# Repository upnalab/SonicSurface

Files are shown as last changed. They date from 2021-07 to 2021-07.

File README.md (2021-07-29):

# SonicSurface
An Open ultrasonic phased-array for applications in acoustic levitation, haptic feedback, directive audio and many more.

# Contents of this Repository
Algorithms - Algorithms to generate different patterns
Electronics - PCB gerber files and bill of materials
Firmware - Code to be upload in the FPGA boards that control the arrays
Mech - Mechanical parts for 3d printing or lasercutting

# How to Assemble and example Applications
- Instructables: https://www.instructables.com/SonicSurface-Phased-array-for-Levitation-Mid-air-T/
- Video: https://www.youtube.com/watch?v=vAEZvYlUnEM
- Paper: https://doi.org/10.3390/app11072981

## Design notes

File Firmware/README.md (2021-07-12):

FPGA jic are the code to upload into the FPGA using the Blaster device (or any other compatible one) they are the precompiled verions of what is in the project folder. They have no phase calibration for the emitters so you should do one of the following:
1) solder the transducers with the right polarity
2) put the phase calibration on the simulation
3) recompile the project into a new jic with the calibration hardcoded

FPGAPrimary is enabled with the command 192 and generates its own clock on port D
FPGASecondary is enabled with the command 192 and syncs its clock with what is input in port A
FPGATactileModulation is a Primary board that modulates the emitted waves at 200Hz (or at a config speed). 

ESP contain optional controllers. The haptic controller is designed to be used with FPGATactileModulation

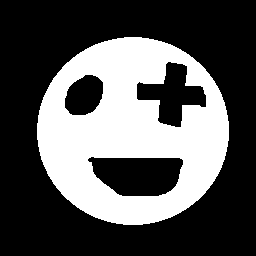
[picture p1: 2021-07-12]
Algorithms/EmissionPhasesAmpsForTargetSlice/smiley.png

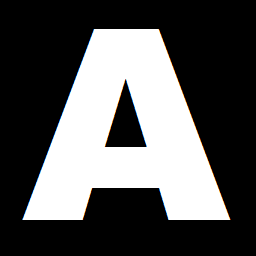
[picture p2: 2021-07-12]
Algorithms/EmissionPhasesAmpsForTargetSlice/target_a.png

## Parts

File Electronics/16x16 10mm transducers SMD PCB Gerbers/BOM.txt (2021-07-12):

the size of the PCB is 183 x 169mm 2 layers

128x MIC4127 SOIC8
32x 74hc595 SOIC16
160x 0.1uf capacitors 50v 0805
1x dc barrel
head connectors for the FPGA (2x22) and lateral connectors

256x transducers ideally the ones used for TinyLev (Check for Instructables Acoustic Levitator)

Other pin compatible drivers are: TC4427a or MIC4127  / MIC4478 for 32V but pricey as hell

The FPGA is this one: https://www.waveshare.com/coreep4ce6.htm

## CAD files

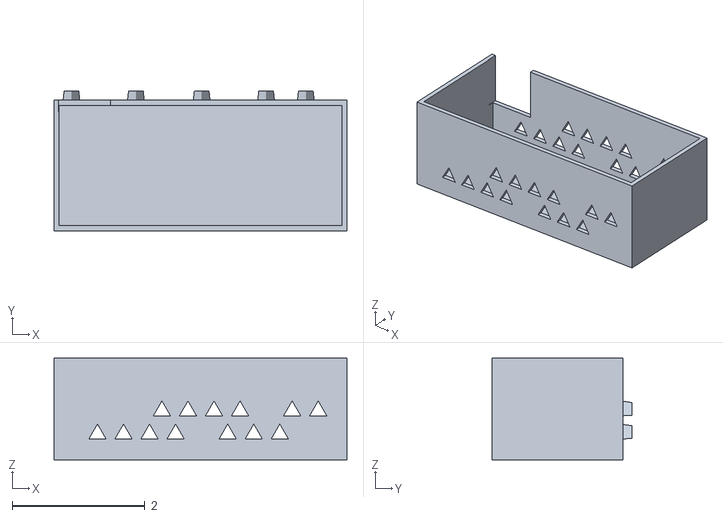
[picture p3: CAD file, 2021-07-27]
Mech/board case/SonicSurfaceHolder.stl
4.41 x 2.10 x 1.53

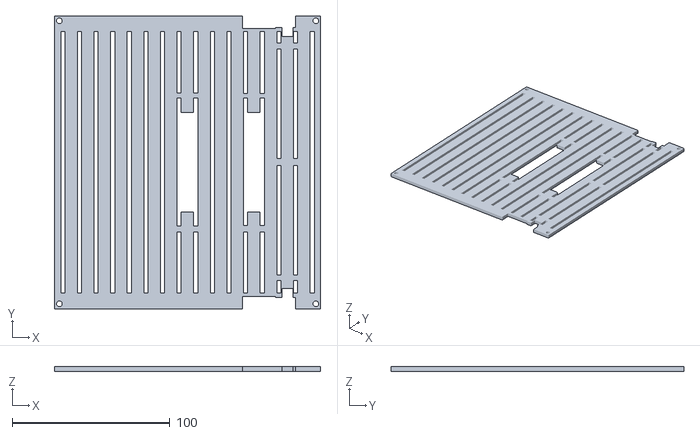
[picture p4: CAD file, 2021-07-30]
Mech/spacer/3d printed spacer.stl
168.5 x 185.5 x 3.00

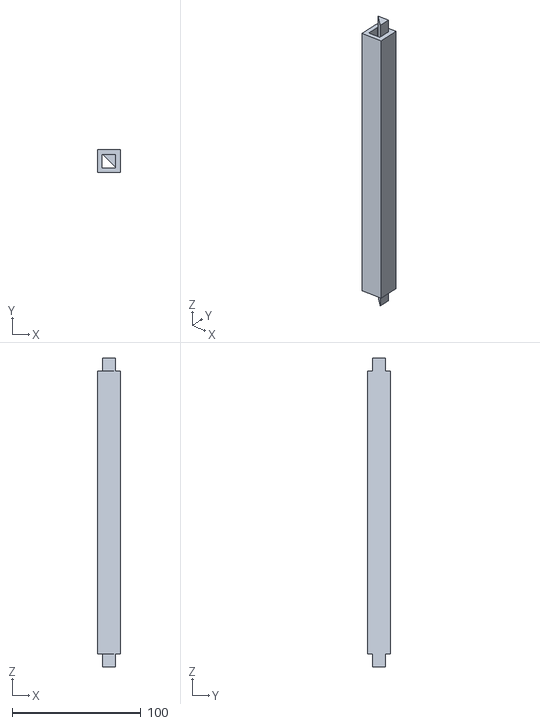
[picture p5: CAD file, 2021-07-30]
Mech/two arrays support/column.stl
18.0 x 18.0 x 240.0

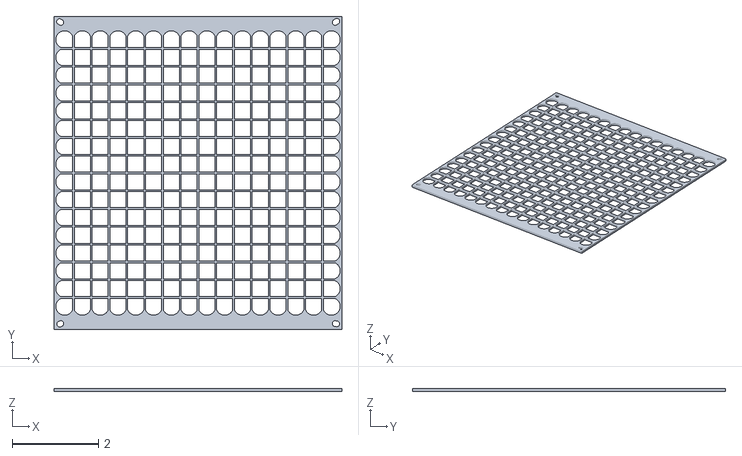
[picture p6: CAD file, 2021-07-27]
Mech/board case/SonicSurfaceGrid.stl
6.69 x 7.28 x 0.0796

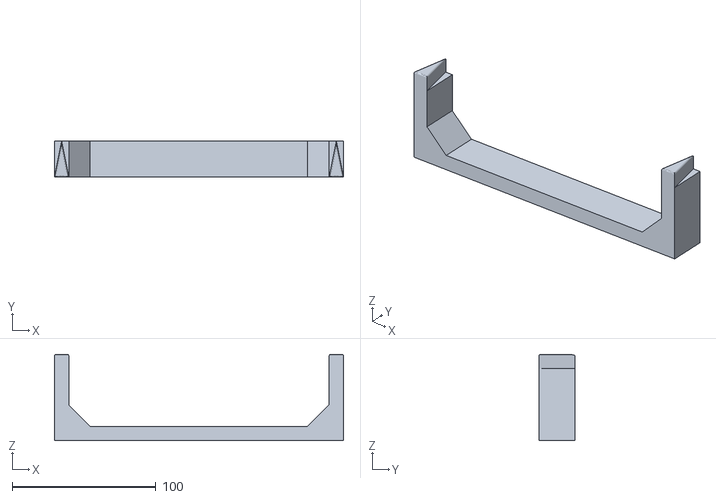
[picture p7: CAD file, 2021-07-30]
Mech/two arrays support/leg.stl
201.0 x 25.0 x 60.0

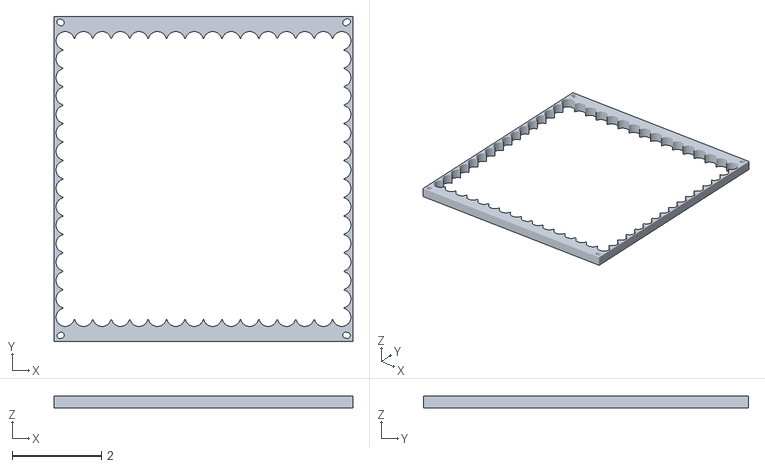
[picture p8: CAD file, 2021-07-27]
Mech/board case/SonicSpacer.stl
6.69 x 7.28 x 0.276

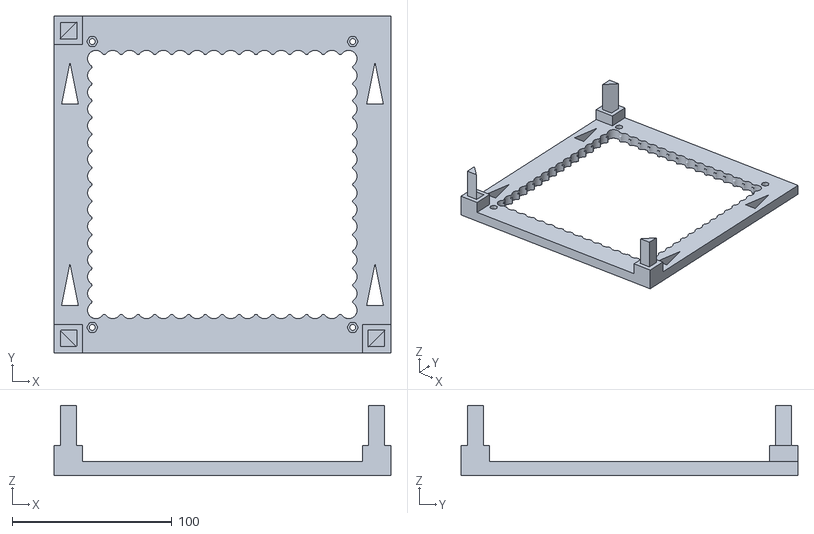
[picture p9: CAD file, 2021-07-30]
Mech/two arrays support/base.stl
211.0 x 211.0 x 44.0

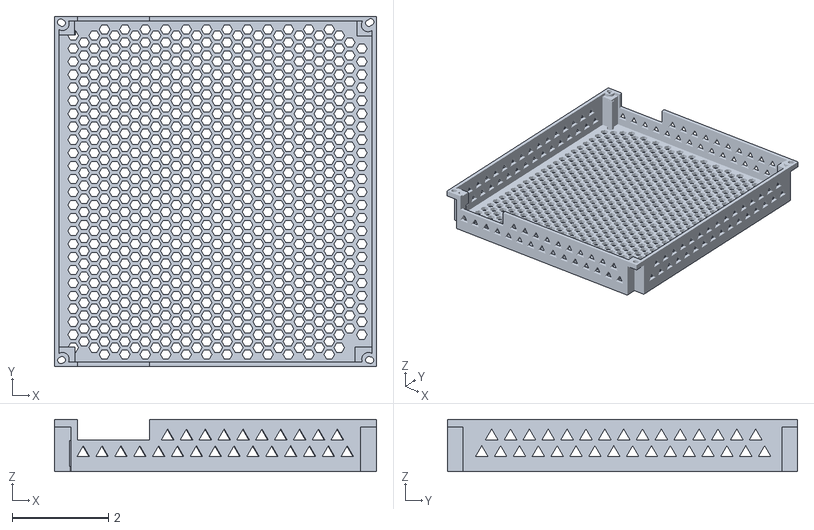
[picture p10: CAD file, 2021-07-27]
Mech/board case/SonicBox.stl
6.69 x 7.28 x 1.08

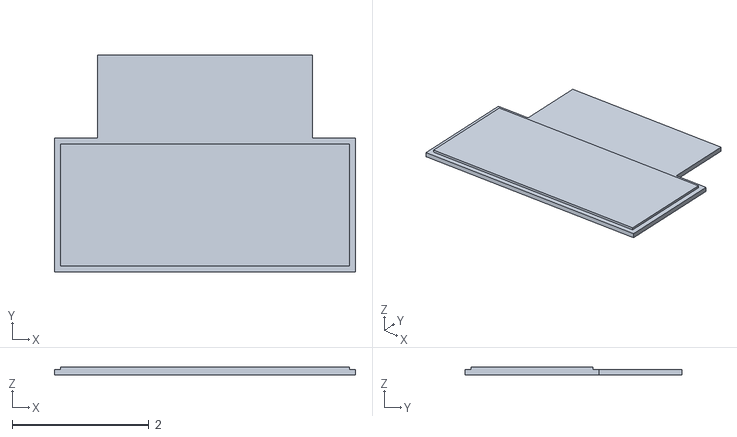
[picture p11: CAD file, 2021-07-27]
Mech/board case/SonicSurfaceHolderLid.stl
4.41 x 3.18 x 0.118

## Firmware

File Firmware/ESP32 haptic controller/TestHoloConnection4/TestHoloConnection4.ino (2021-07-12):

#include "WiFi.h"


#define ULTRATACT_VERSION "2.1"
const char* ssid = "UltraTactile Master";
const char* ssidMaster = "UltraTactile Master";
const char* password = "12345678";
#define BUTTON_PIN 12
#define MOD_PERIODS_DEFAULT 10

WiFiServer server(80);

#define N_TRANS 256
const float TRANS_POS[N_TRANS*3] = { -0.078749985, 0.0, 0.07874999, -0.05774999, 0.0, 0.07874999, -0.04724999, 0.0, 0.07874999, -0.068249986, 0.0, 0.06824999, -0.078749985, 0.0, 0.06824999, -0.04724999, 0.0, 0.06824999, -0.05774999, 0.0, 0.06824999, -0.068249986, 0.0, 0.07874999, -0.078749985, 0.0, 0.057749998, -0.05774999, 0.0, 0.057749998, -0.04724999, 0.0, 0.057749998, -0.068249986, 0.0, 0.04725, -0.078749985, 0.0, 0.04725, -0.04724999, 0.0, 0.04725, -0.05774999, 0.0, 0.04725, -0.068249986, 0.0, 0.057749998, -0.078749985, 0.0, 0.036750004, -0.05774999, 0.0, 0.036750004, -0.04724999, 0.0, 0.036750004, -0.068249986, 0.0, 0.026250003, -0.078749985, 0.0, 0.026250003, -0.04724999, 0.0, 0.026250003, -0.05774999, 0.0, 0.026250003, -0.068249986, 0.0, 0.036750004, -0.078749985, 0.0, 0.015750004, -0.05774999, 0.0, 0.015750004, -0.04724999, 0.0, 0.015750004, -0.068249986, 0.0, 0.0052500046, -0.078749985, 0.0, 0.0052500046, -0.04724999, 0.0, 0.0052500046, -0.05774999, 0.0, 0.0052500046, -0.068249986, 0.0, 0.015750004, -0.078749985, 0.0, -0.005249995, -0.05774999, 0.0, -0.005249995, -0.04724999, 0.0, -0.005249995, -0.068249986, 0.0, -0.015749995, -0.078749985, 0.0, -0.015749995, -0.04724999, 0.0, -0.015749995, -0.05774999, 0.0, -0.015749995, -0.068249986, 0.0, -0.005249995, -0.078749985, 0.0, -0.026249994, -0.05774999, 0.0, -0.026249994, -0.04724999, 0.0, -0.026249994, -0.068249986, 0.0, -0.036749996, -0.078749985, 0.0, -0.036749996, -0.04724999, 0.0, -0.036749996, -0.05774999, 0.0, -0.036749996, -0.068249986, 0.0, -0.026249994, -0.078749985, 0.0, -0.04724999, -0.05774999, 0.0, -0.04724999, -0.04724999, 0.0, -0.04724999, -0.068249986, 0.0, -0.05774999, -0.078749985, 0.0, -0.05774999, -0.04724999, 0.0, -0.05774999, -0.05774999, 0.0, -0.05774999, -0.068249986, 0.0, -0.04724999, -0.078749985, 0.0, -0.068249986, -0.05774999, 0.0, -0.068249986, -0.04724999, 0.0, -0.068249986, -0.068249986, 0.0, -0.078749985, -0.078749985, 0.0, -0.078749985, -0.04724999, 0.0, -0.078749985, -0.05774999, 0.0, -0.078749985, -0.068249986, 0.0, -0.068249986, -0.036749996, 0.0, 0.07874999, -0.015749995, 0.0, 0.07874999, -0.005249995, 0.0, 0.07874999, -0.026249994, 0.0, 0.06824999, -0.036749996, 0.0, 0.06824999, -0.005249995, 0.0, 0.06824999, -0.015749995, 0.0, 0.06824999, -0.026249994, 0.0, 0.07874999, -0.036749996, 0.0, 0.057749998, -0.015749995, 0.0, 0.057749998, -0.005249995, 0.0, 0.057749998, -0.026249994, 0.0, 0.04725, -0.036749996, 0.0, 0.04725, -0.005249995, 0.0, 0.04725, -0.015749995, 0.0, 0.04725, -0.026249994, 0.0, 0.057749998, -0.036749996, 0.0, 0.036750004, -0.015749995, 0.0, 0.036750004, -0.005249995, 0.0, 0.036750004, -0.026249994, 0.0, 0.026250003, -0.036749996, 0.0, 0.026250003, -0.005249995, 0.0, 0.026250003, -0.015749995, 0.0, 0.026250003, -0.026249994, 0.0, 0.036750004, -0.036749996, 0.0, 0.015750004, -0.015749995, 0.0, 0.015750004, -0.005249995, 0.0, 0.015750004, -0.026249994, 0.0, 0.0052500046, -0.036749996, 0.0, 0.0052500046, -0.005249995, 0.0, 0.0052500046, -0.015749995, 0.0, 0.0052500046, -0.026249994, 0.0, 0.015750004, -0.036749996, 0.0, -0.005249995, -0.015749995, 0.0, -0.005249995, -0.005249995, 0.0, -0.005249995, -0.026249994, 0.0, -0.015749995, -0.036749996, 0.0, -0.015749995, -0.005249995, 0.0, -0.015749995, -0.015749995, 0.0, -0.015749995, -0.026249994, 0.0, -0.005249995, -0.036749996, 0.0, -0.026249994, -0.015749995, 0.0, -0.026249994, -0.005249995, 0.0, -0.026249994, -0.026249994, 0.0, -0.036749996, -0.036749996, 0.0, -0.036749996, -0.005249995, 0.0, -0.036749996, -0.015749995, 0.0, -0.036749996, -0.026249994, 0.0, -0.026249994, -0.036749996, 0.0, -0.04724999, -0.015749995, 0.0, -0.04724999, -0.005249995, 0.0, -0.04724999, -0.026249994, 0.0, -0.05774999, -0.036749996, 0.0, -0.05774999, -0.005249995, 0.0, -0.05774999, -0.015749995, 0.0, -0.05774999, -0.026249994, 0.0, -0.04724999, -0.036749996, 0.0, -0.068249986, -0.015749995, 0.0, -0.068249986, -0.005249995, 0.0, -0.068249986, -0.026249994, 0.0, -0.078749985, -0.036749996, 0.0, -0.078749985, -0.005249995, 0.0, -0.078749985, -0.015749995, 0.0, -0.078749985, -0.026249994, 0.0, -0.068249986, 0.0052500046, 0.0, 0.07874999, 0.026250003, 0.0, 0.07874999, 0.036750004, 0.0, 0.07874999, 0.015750004, 0.0, 0.06824999, 0.0052500046, 0.0, 0.06824999, 0.036750004, 0.0, 0.06824999, 0.026250003, 0.0, 0.06824999, 0.015750004, 0.0, 0.07874999, 0.0052500046, 0.0, 0.057749998, 0.026250003, 0.0, 0.057749998, 0.036750004, 0.0, 0.057749998, 0.015750004, 0.0, 0.04725, 0.0052500046, 0.0, 0.04725, 0.036750004, 0.0, 0.04725, 0.026250003, 0.0, 0.04725, 0.015750004, 0.0, 0.057749998, 0.0052500046, 0.0, 0.036750004, 0.026250003, 0.0, 0.036750004, 0.036750004, 0.0, 0.036750004, 0.015750004, 0.0, 0.026250003, 0.0052500046, 0.0, 0.026250003, 0.036750004, 0.0, 0.026250003, 0.026250003, 0.0, 0.026250003, 0.015750004, 0.0, 0.036750004, 0.0052500046, 0.0, 0.015750004, 0.026250003, 0.0, 0.015750004, 0.036750004, 0.0, 0.015750004, 0.015750004, 0.0, 0.0052500046, 0.0052500046, 0.0, 0.0052500046, 0.036750004, 0.0, 0.0052500046, 0.026250003, 0.0, 0.0052500046, 0.015750004, 0.0, 0.015750004, 0.0052500046, 0.0, -0.005249995, 0.026250003, 0.0, -0.005249995, 0.036750004, 0.0, -0.005249995, 0.015750004, 0.0, -0.015749995, 0.0052500046, 0.0, -0.015749995, 0.036750004, 0.0, -0.015749995, 0.026250003, 0.0, -0.015749995, 0.015750004, 0.0, -0.005249995, 0.0052500046, 0.0, -0.026249994, 0.026250003, 0.0, -0.026249994, 0.036750004, 0.0, -0.026249994, 0.015750004, 0.0, -0.036749996, 0.0052500046, 0.0, -0.036749996, 0.036750004, 0.0, -0.036749996, 0.026250003, 0.0, -0.036749996, 0.015750004, 0.0, -0.026249994, 0.0052500046, 0.0, -0.04724999, 0.026250003, 0.0, -0.04724999, 0.036750004, 0.0, -0.04724999, 0.015750004, 0.0, -0.05774999, 0.0052500046, 0.0, -0.05774999, 0.036750004, 0.0, -0.05774999, 0.026250003, 0.0, -0.05774999, 0.015750004, 0.0, -0.04724999, 0.0052500046, 0.0, -0.068249986, 0.026250003, 0.0, -0.068249986, 0.036750004, 0.0, -0.068249986, 0.015750004, 0.0, -0.078749985, 0.0052500046, 0.0, -0.078749985, 0.036750004, 0.0, -0.078749985, 0.026250003, 0.0, -0.078749985, 0.015750004, 0.0, -0.068249986, 0.04725, 0.0, 0.07874999, 0.06824999, 0.0, 0.07874999, 0.07874999, 0.0, 0.07874999, 0.057749998, 0.0, 0.06824999, 0.04725, 0.0, 0.06824999, 0.07874999, 0.0, 0.06824999, 0.06824999, 0.0, 0.06824999, 0.057749998, 0.0, 0.07874999, 0.04725, 0.0, 0.057749998, 0.06824999, 0.0, 0.057749998, 0.07874999, 0.0, 0.057749998, 0.057749998, 0.0, 0.04725, 0.04725, 0.0, 0.04725, 0.07874999, 0.0, 0.04725, 0.06824999, 0.0, 0.04725, 0.057749998, 0.0, 0.057749998, 0.04725, 0.0, 0.036750004, 0.06824999, 0.0, 0.036750004, 0.07874999, 0.0, 0.036750004, 0.057749998, 0.0, 0.026250003, 0.04725, 0.0, 0.026250003, 0.07874999, 0.0, 0.026250003, 0.06824999, 0.0, 0.026250003, 0.057749998, 0.0, 0.036750004, 0.04725, 0.0, 0.015750004, 0.06824999, 0.0, 0.015750004, 0.07874999, 0.0, 0.015750004, 0.057749998, 0.0, 0.0052500046, 0.04725, 0.0, 0.0052500046, 0.07874999, 0.0, 0.0052500046, 0.06824999, 0.0, 0.0052500046, 0.057749998, 0.0, 0.015750004, 0.04725, 0.0, -0.005249995, 0.06824999, 0.0, -0.005249995, 0.07874999, 0.0, -0.005249995, 0.057749998, 0.0, -0.015749995, 0.04725, 0.0, -0.015749995, 0.07874999, 0.0, -0.015749995, 0.06824999, 0.0, -0.015749995, 0.057749998, 0.0, -0.005249995, 0.04725, 0.0, -0.026249994, 0.06824999, 0.0, -0.026249994, 0.07874999, 0.0, -0.026249994, 0.057749998, 0.0, -0.036749996, 0.04725, 0.0, -0.036749996, 0.07874999, 0.0, -0.036749996, 0.06824999, 0.0, -0.036749996, 0.057749998, 0.0, -0.026249994, 0.04725, 0.0, -0.04724999, 0.06824999, 0.0, -0.04724999, 0.07874999, 0.0, -0.04724999, 0.057749998, 0.0, -0.05774999, 0.04725, 0.0, -0.05774999, 0.07874999, 0.0, -0.05774999, 0.06824999, 0.0, -0.05774999, 0.057749998, 0.0, -0.04724999, 0.04725, 0.0, -0.068249986, 0.06824999, 0.0, -0.068249986, 0.07874999, 0.0, -0.068249986, 0.057749998, 0.0, -0.078749985, 0.04725, 0.0, -0.078749985, 0.07874999, 0.0, -0.078749985, 0.06824999, 0.0, -0.078749985, 0.057749998, 0.0, -0.068249986};
const byte PHASES_FOR_LINE[N_TRANS] = {14,6,20,15,3,10,27,24,20,14,29,22,4,14,31,5,16,14,28,14,25,6,26,4,0,2,14,25,3,18,7,21,3,7,18,21,0,14,2,25,25,26,6,4,16,28,14,14,4,31,14,5,20,29,14,22,3,27,10,24,14,20,6,15,31,0,2,28,21,25,22,3,9,11,14,3,26,0,29,17,9,12,15,29,20,26,23,18,27,31,2,9,31,6,3,5,31,3,6,5,27,2,31,9,20,23,26,18,9,15,12,29,26,29,0,17,9,14,11,3,21,22,25,3,31,2,0,28,3,9,0,5,25,22,31,14,14,19,10,11,0,27,5,25,15,19,10,5,26,21,31,26,2,6,29,17,6,0,10,13,6,10,0,13,2,29,6,17,26,31,21,26,15,10,19,5,0,5,27,25,14,10,19,11,25,31,22,14,3,0,9,5,21,3,17,8,11,5,24,17,0,10,22,11,19,5,26,27,4,6,17,3,16,27,16,25,25,23,2,14,29,5,26,10,29,26,5,10,25,2,23,14,16,16,27,25,4,17,6,3,19,26,5,27,0,22,10,11,11,24,5,17,21,17,3,8};

byte bufferToSend[N_TRANS + 2];

unsigned long millisFromLastButtonPress = 0;
byte buttonPresses = 0;

/* Array control functions */

void swichOffArray() {
  bufferToSend[0] = 254; //start phases command
  bufferToSend[N_TRANS + 1] = 253; //swap double buffer command (like a commit)
  for (int i = 1; i < N_TRANS + 1; i += 1)
    bufferToSend[i] = 32; //32 is the value for switching of the transducer
  Serial2.write( bufferToSend, N_TRANS + 2 );
  Serial2.flush();
}

void changeModulation(byte periods){
  if (periods < 1) periods = 1;
  else if(periods > 31) periods = 31;
  Serial2.write( 0b10100000 | periods);
}

const float WAVELENGTH = 0.00865f;
const float PHASE_DIV = 32.0f;
void focusArrayAt(const float posX, const float posY, const float posZ) { //positions are in meters in respect to the center of the array
  bufferToSend[0] = 254; //start phases command
  bufferToSend[N_TRANS + 1] = 253; //swap double buffer command (i.e. commit)
  for (int i = 1; i < N_TRANS+1; i += 1) {
    const float diffX = TRANS_POS[(i-1)*3 + 0] - posX;
    const float diffY = TRANS_POS[(i-1)*3 + 1] - posY;
    const float diffZ = TRANS_POS[(i-1)*3 + 2] - posZ;
    const float distInWavelengths = sqrt(diffX * diffX + diffY * diffY + diffZ * diffZ) / WAVELENGTH;
    const byte phase = (byte)((ceil(distInWavelengths) - distInWavelengths) * PHASE_DIV);
    bufferToSend[i] = phase;
  }
  Serial2.write( bufferToSend, N_TRANS + 2 );
  Serial2.flush();
}

void makeBeeps(int nBeeps, int modulation=7){
  if (nBeeps < 1) nBeeps = 1;
  else if(nBeeps > 10) nBeeps = 10;
  
  swichOffArray();
  changeModulation( modulation );
  for (int i = 0; i < nBeeps; i+=1 ){
    focusArrayAt(0,0.1,0);
    delay(250);
    swichOffArray();
    delay(250);
  }
  changeModulation( MOD_PERIODS_DEFAULT );
}




void sendPhasePattern(const byte* pattern){
  Serial2.write( 254 );
  Serial2.write( pattern, N_TRANS);
  Serial2.write( 253 );
  Serial2.flush();
}

/* Network functions*/

void configWifiAsAccessPoint(const char* ssidName){
  Serial.println("Configuring as access point...");
  WiFi.mode(WIFI_AP);
  WiFi.softAP( ssidName, password );
  Serial.println("Wait 100 ms for AP_START...");
  delay(100);
  
  Serial.println("Set softAPConfig");
  IPAddress Ip(192, 168, 1, 1);
  IPAddress NMask(255, 255, 255, 0);
  WiFi.softAPConfig(Ip, Ip, NMask);
  IPAddress myIP = WiFi.softAPIP();
  Serial.print("AP IP address: ");
  Serial.println(myIP);
}
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

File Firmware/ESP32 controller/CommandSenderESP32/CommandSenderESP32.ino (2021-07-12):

#include "WiFi.h"

#include "EmitterPos.h"
#include "FocusAlg.h"
#include "PointsMov.h"

#define ESPFOCAL_VERSION "0.0"

#define BUTTON_PIN 12


/* Array control functions */
int ibpIterations = 4;
byte buff[N_EMITTERS]; //phases to be emitted
float pointPos[MAX_POINTS * 3];

void switchOnArray(boolean onTop, boolean onBottom);
void switchBuffer();
void sendBuffer();
void sendPhases(String command);

void processCommand(String command);

int parseFloats(String s, int startIndex, float target[], int maxNumbers);

/* Network functions*/

const char* ssid = "FOCAL_ESP";
const char* password = "12345678";
WiFiServer server(80);

void configWifiAsAccessPoint(const char* ssidName) {
  Serial.println("Configuring as access point...");
  WiFi.mode(WIFI_AP);
  WiFi.softAP( ssidName, password );
  Serial.println("Wait 100 ms for AP_START...");
  delay(100);

  Serial.println("Set softAPConfig");
  IPAddress Ip(192, 168, 1, 1);
  IPAddress NMask(255, 255, 255, 0);
  WiFi.softAPConfig(Ip, Ip, NMask);
  IPAddress myIP = WiFi.softAPIP();
  Serial.print("AP IP address: ");
  Serial.println(myIP);
}


/* Setup*/
void setup() {
  Serial.begin(230400); // this serial is for receiving commands and sending debug info to the computer
  Serial2.begin(230400, SERIAL_8N1, 17, 16); //RX2 TX2 This serial communicates with the array
  pinMode(BUTTON_PIN, INPUT_PULLUP);
  Serial.println(ESPFOCAL_VERSION);
  Serial.println( ssid );

  configWifiAsAccessPoint( ssid ); //start as access point with regular ssid
  server.begin();
  delay(200);

  Serial2.write( 151 ); //switch on the FPGA clocks (in case that they were off with the 150 command send at random during start up)
  Serial.println("Switching off the array...");
  switchOnArray(false, false);

  ibp_initEmitters();
}


void focusArrayAtPoints() {
  //this is the IBP method. slow but stronger trapping points. hard to join at closer distances.
  ibp_initPropagators(2, pointPos);
  for (int i = 0; i < ibpIterations; ++i)
    ibp_iterate( 2 );
  ibp_applySolution(2, buff);
  
  
  //this is the other method. faster, works at closer distances but not as strong
  //multiFocusAt(2,  pointPos,  buff);

  sendBuffer();
}

int previousButton = HIGH;
int cyclesButtonHigh = 0;
enum ePointsStatus {statusOff, statusFocus, statusMoving};
ePointsStatus currentStatus = statusOff;
void loop() {

  /* button press */
  const int currentButtonState = digitalRead(BUTTON_PIN);
  if (previousButton == HIGH && currentButtonState == LOW && cyclesButtonHigh > 100) { //when the button is pressed. last part is for debouncing
    cyclesButtonHigh = 0;
    /* button has been pressed*/
    Serial.println("Button has been pressed");
    if (currentStatus == statusOff) {
      Serial.println("Focusing points");
      currentStatus = statusFocus;
      points_reset(2, pointPos, POINTS_MOV_SEP, ARRAY_HEIGHT/2 );
      focusArrayAtPoints();
    } else if (currentStatus == statusFocus) {
      Serial.println("Moving");
      currentStatus = statusMoving;
    } else if (currentStatus == statusMoving) {
      Serial.println("Off");
      currentStatus = statusOff;
      switchOnArray(false, false);
    }
  }
  if (currentButtonState == HIGH && cyclesButtonHigh < 0xFF) {
    cyclesButtonHigh += 1;
  } else if (currentButtonState == LOW) {
    cyclesButtonHigh = 0;
  }
  previousButton = currentButtonState;
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

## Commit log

2021-07-27 Added the STLs for the case of a single board.
    [SonicBox.stl, SonicSpacer.stl, SonicSurfaceGrid.stl, SonicSurfaceHolder.stl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]
2021-07-30 Added STL file for the two arrays setup
    [base.stl, column.stl, leg.stl]
2021-07-30 Updated 3d printed spacer
    [3d printed spacer.stl]
